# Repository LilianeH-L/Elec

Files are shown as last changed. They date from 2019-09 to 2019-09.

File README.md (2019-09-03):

# Metis-Elec

Repositories pour de le code de l'équipe électrique les trois équipes sont : 

- Acquisiton 
    - Capter les signaux EMG du patient pour le transmettre au Jetson

- Moor_Control
    - Contrôle de la position de tous les moteurs pour ateindre la position désiré

- BLDC_Driver
    - Contrôle individuelle de chaque moteur BLDC pour qu'il soit à la position recquise.

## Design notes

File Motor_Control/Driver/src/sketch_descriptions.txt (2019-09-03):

elctrodesRead : Lecture d'une electrode sur le bicep pour controller un le moteur
elctrodesRead_2 : Lecture d'une electrode sur le bicep pour controller un le moteur

motorController_main : 
motorController_master : Send a command to the motor
motorController_slave : 
motorTest : To test a motor

oldSketches : Older sketches, not useful anymore

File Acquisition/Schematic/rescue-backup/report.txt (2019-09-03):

Info: Backing up file “C:\Users\Victor\Documents\Ecole\Projets\Metis\Metis-Exoskeleton\Acquisition\Schematic\sym-lib-table” to file “C:\Users\Victor\Documents\Ecole\Projets\Metis\Metis-Exoskeleton\Acquisition\Schematic\rescue-backup\sym-lib-table-2018-11-21-18-34-24”.
Info: Backing up file “C:\Users\Victor\Documents\Ecole\Projets\Metis\Metis-Exoskeleton\Acquisition\Schematic\AmpFil3a.sch” to file “C:\Users\Victor\Documents\Ecole\Projets\Metis\Metis-Exoskeleton\Acquisition\Schematic\rescue-backup\AmpFil3a-2018-11-21-18-34-24.sch”.
Info: Backing up file “C:\Users\Victor\Documents\Ecole\Projets\Metis\Metis-Exoskeleton\Acquisition\Schematic\AmpFil3a.pro” to file “C:\Users\Victor\Documents\Ecole\Projets\Metis\Metis-Exoskeleton\Acquisition\Schematic\rescue-backup\AmpFil3a-2018-11-21-18-34-24.pro”.
Info: Backing up file “C:\Users\Victor\Documents\Ecole\Projets\Metis\Metis-Exoskeleton\Acquisition\Schematic\AmpFil3a-cache.lib” to file “C:\Users\Victor\Documents\Ecole\Projets\Metis\Metis-Exoskeleton\Acquisition\Schematic\rescue-backup\AmpFil3a-cache-2018-11-21-18-34-24.lib”.
Info: Backing up file “C:\Users\Victor\Documents\Ecole\Projets\Metis\Metis-Exoskeleton\Acquisition\Schematic\AmpFil3a-rescue.lib” to file “C:\Users\Victor\Documents\Ecole\Projets\Metis\Metis-Exoskeleton\Acquisition\Schematic\rescue-backup\AmpFil3a-rescue-2018-11-21-18-34-24.lib”.
Info: Backing up file “C:\Users\Victor\Documents\Ecole\Projets\Metis\Metis-Exoskeleton\Acquisition\Schematic\AmpFil3a-rescue.dcm” to file “C:\Users\Victor\Documents\Ecole\Projets\Metis\Metis-Exoskeleton\Acquisition\Schematic\rescue-backup\AmpFil3a-rescue-2018-11-21-18-34-24.dcm”.
Info: Adding library “AmpFil3a-rescue”, file “${KIPRJMOD}/AmpFil3a-rescue.lib” to project symbol library table.
Symbol “LM324” mapped to symbol library “AmpFil3a-rescue”.
Symbol “R” mapped to symbol library “AmpFil3a-rescue”.
Symbol “R” mapped to symbol library “AmpFil3a-rescue”.
Symbol “R” mapped to symbol library “AmpFil3a-rescue”.
Symbol “R” mapped to symbol library “AmpFil3a-rescue”.
Symbol “GNDREF” mapped to symbol library “AmpFil3a-rescue”.
Symbol “GNDREF” mapped to symbol library “AmpFil3a-rescue”.
Symbol “C” mapped to symbol library “AmpFil3a-rescue”.
Symbol “INA128” mapped to symbol library “AmpFil3a-rescue”.
Symbol “R” mapped to symbol library “AmpFil3a-rescue”.
Symbol “LM324” mapped to symbol library “AmpFil3a-rescue”.
Symbol “C” mapped to symbol library “AmpFil3a-rescue”.
Symbol “R” mapped to symbol library “AmpFil3a-rescue”.
Symbol “R” mapped to symbol library “AmpFil3a-rescue”.
Symbol “GNDREF” mapped to symbol library “AmpFil3a-rescue”.
Symbol “R” mapped to symbol library “AmpFil3a-rescue”.
Symbol “LM324” mapped to symbol library “AmpFil3a-rescue”.
Symbol “C” mapped to symbol library “AmpFil3a-rescue”.
Symbol “GNDREF” mapped to symbol library “AmpFil3a-rescue”.
Symbol “R” mapped to symbol library “AmpFil3a-rescue”.
Symbol “GNDREF” mapped to symbol library “AmpFil3a-rescue”.
Symbol “Audio-Jack-3” mapped to symbol library “AmpFil3a-rescue”.
Symbol “Conn_01x03” mapped to symbol library “AmpFil3a-rescue”.
Symbol “R” mapped to symbol library “AmpFil3a-rescue”.
Symbol “R” mapped to symbol library “AmpFil3a-rescue”.
Symbol “R” mapped to symbol library “AmpFil3a-rescue”.
Info: Symbol library table mapping complete!

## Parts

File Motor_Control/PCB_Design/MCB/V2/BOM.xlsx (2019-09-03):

Commande Digikey
Qté | Coût | Qté à commander | Coût total | Référence | Description | # Digikey
6 | $2.31 | 6 | $13.86 | Q1-Q6 | N MOSFET | IRLB8743PBF
5 | $0.01 | 5 | $0.05 | R1-R5 | 1K Resistor, 1206 | RNCP1206FTD1K00TR-ND
1 | $1.73 | 1 | $1.73 | R6 | 0.025R Resistor, 5W, 2512 | 2019-TLRH3APTTE25L0FCT-ND
2 | $0.10 | 2 | $0.20 | C1,C3,C6 | 0.1uF Cap |  | Nombre de board à monter | 1
1 | $0.10 | 1 | $0.10 | C2 | 470 uF Electrolytique |  | Coût total | $60.62
2 | $0.10 | 2 | $0.20 | C4,C5 | 1uF Cap
1 | $4.35 | 1 | $4.35 | U1 | DRV8308 | DRV8308RHAR
2 | $1.68 | 2 | $3.36 |  | DIP, Female | XG4M-1030-T
1 | $1.94 | 1 | $1.94 | - | DIP, Male | XG4A-1034
1 | $0.85 | 1 | $0.85 |  | Molex, Female | 353180820
2 | $0.61 | 2 | $1.22 | - | Molex, Male | 39012080
8 | $0.26 | 8 | $2.08 | - | Molex, 22-28 crimp | 39-00-0047
14 | $0.27 | 14 | $3.78 | - | Molex, 18-24 crimp | 39-00-0039
1 | $1.27 | 1 | $1.27 | - | Ribbon Cable, 10, 1' | 3365/10 300
10 | $0.92 | 10 | $9.20 | - | 18 awg wire, 10' | 81044/12-18-9
1 | $2.04 | 1 | $2.04 | - | Male Headers, 40 | 61304011121
1 | $4.80 | 1 | $4.80 |  | SN75175 | SN75175N
1 | $0.89 | 1 | $0.89 |  | SN74LVC245A | SN74LVC245AN
1 | $2.31 | 1 | $2.31 |  | Female Header, 32 | 61303211821
2 | $2.47 | 2 | $4.94 |  | Molex 3, Female | 39303037
2 | $0.72 | 2 | $1.44 |  | Molex 3, Male | 39014031
 | *Rsense : 696-1675-1-ND. 3W

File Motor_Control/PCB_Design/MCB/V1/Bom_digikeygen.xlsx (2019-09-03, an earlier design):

Manufacturer Part Number | Manufacturer | Digi-Key Part Number | Customer Reference | Reference Designator | Packaging | Part Status | Quantity | Unit Price | Extended Price | Quantity Available | Description
IRLB8743PBF | Infineon Technologies | IRLB8743PBF-ND |  | Q1-Q6 | Tube | Active | 6 | 2.31 | $13.86 | 10058 | MOSFET N-CH 30V 78A TO220AB
CF14JT1K00 | Stackpole Electronics Inc | CF14JT1K00CT-ND |  | R1-R5 | Cut Tape (CT) | Active | 5 | 0.15 | $0.75 | 928873 | RES 1K OHM 1/4W 5% AXIAL
630HR025E | Ohmite | 630HR025E-ND |  | R6 | Bulk | Active | 1 | 1.4 | $1.40 | 5138 | RES 0.025 OHM 3W 3% AXIAL
RDER71E104K0K1H03B | Murata Electronics North America | 490-8808-ND |  | C1,C3,C6 | Bulk | Active | 2 | 0.6 | $1.20 | 3313 | CAP CER 0.1UF 25V X7R RADIAL
UKL1E471KHD | Nichicon | 493-13401-ND |  | C2 | Bulk | Active | 1 | 1.26 | $1.26 | 756 | CAP ALUM 470UF 10% 25V RADIAL
FG18X7R1E105KRT06 | TDK Corporation | 445-173261-1-ND |  | C4,C5 | Cut Tape (CT) | Active | 2 | 0.45 | $0.90 | 7135 | CAP CER 1UF 25V X7R RADIAL
DRV8308RHAR | Texas Instruments | 296-37834-1-ND |  | U1 | Cut Tape (CT) | Active | 1 | 4.35 | $4.35 | 257 | IC MOTOR DRIVER 8.5V-32V 40VQFN
XG4M-1030-T | Omron Electronics Inc-EMC Div | OR909-ND |  |  | Tray | Active | 2 | 1.68 | $3.36 | 27951 | CONN RCPT 10POS IDC 28AWG GOLD
XG4A-1034 | Omron Electronics Inc-EMC Div | OR1001-ND |  | - | Tray | Active | 1 | 1.94 | $1.94 | 8374 | CONN HEADER R/A 10POS 2.54MM
0353180820 | Molex | WM13197-ND |  |  | Bag | Active | 1 | 0.85 | $0.85 | 6463 | CONN HEADER R/A 8POS 4.2MM
0039012080 | Molex | WM3703-ND |  | - | Bulk | Active | 2 | 0.61 | $1.22 | 66365 | CONN RECEPT 8POS DUAL
39-00-0047 | Molex | WM2503-ND |  | - | Bulk | Active | 8 | 0.26 | $2.08 | 111858 | CONN SOCKET 22-28AWG CRIMP TIN
39-00-0039 | Molex | WM2501-ND |  | - | Bulk | Active | 14 | 0.257 | $3.59 | 515333 | CONN SOCKET 18-24AWG CRIMP TIN
81044/12-18-9 | TE Connectivity Aerospace, Defense and Marine | A132409-DS-ND |  | - | * | Active | 10 | 0.728 | $7.28 | 4742 | HOOK-UP STRND 18AWG WHITE FT
61304011121 | Wurth Electronics Inc. | 732-5334-ND |  | - | Bag | Active | 1 | 2.04 | $2.04 | 1805 | CONN HEADER VERT 40POS 2.54MM
SN75175N | Texas Instruments | 296-1736-5-ND |  |  | Tube | Active | 1 | 4.8 | $4.80 | 2808 | IC QUAD DIFF LINE RECEIVER 16DIP
SN74LVC245AN | Texas Instruments | 296-8503-5-ND |  |  | Tube | Active | 1 | 0.89 | $0.89 | 3388 | IC TXRX NON-INVERT 3.6V 20DIP
61303211821 | Wurth Electronics Inc. | 732-2860-ND |  |  | Tray | Active | 1 | 2.31 | $2.31 | 257 | CONN HDR 32POS 0.1 GOLD PCB
0039303037 | Molex | WM23935-ND |  |  | Bag | Active | 2 | 2.47 | $4.94 | 1379 | CONN HEADER R/A 3POS 4.2MM
0039014031 | Molex | WM23608-ND |  |  | Bag | Active | 2 | 0.72 | $1.44 | 16106 | CONN RECEPT 3POS VERT SINGLE
3365/10 300 | 3M | 3M157815-5-ND |  |  | Bulk | Active | 1 | 4.54 | $4.54 | 0 | CBL RIBN 10COND 0.050 GRAY 5'
D2816-42 | Harwin Inc. | 952-2211-ND |  |  | Tube | Active | 1 | 1.93 | $1.93 | 630 | CONN IC DIP SOCKET 16POS GOLD
D2820-42 | Harwin Inc. | 952-2213-ND |  |  | Tube | Active | 1 | 2.26 | $2.26 | 84 | CONN IC DIP SOCKET 20POS GOLD

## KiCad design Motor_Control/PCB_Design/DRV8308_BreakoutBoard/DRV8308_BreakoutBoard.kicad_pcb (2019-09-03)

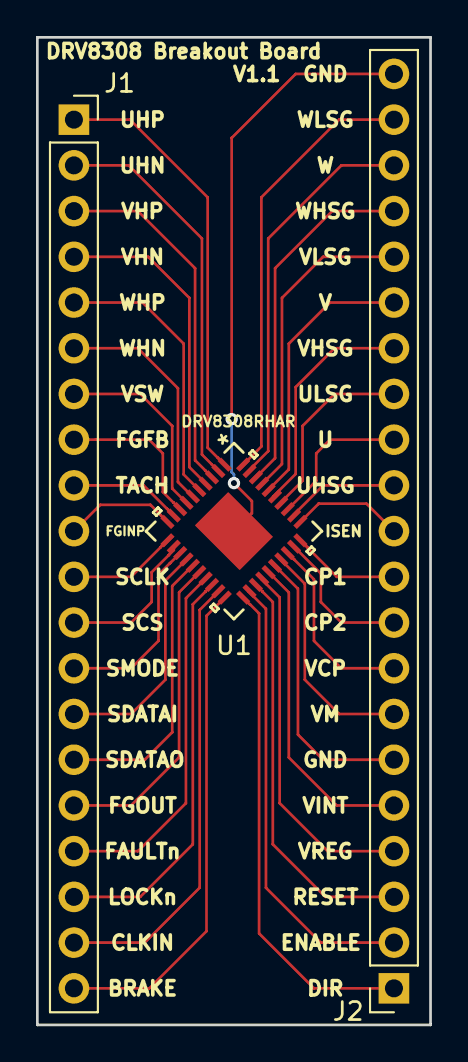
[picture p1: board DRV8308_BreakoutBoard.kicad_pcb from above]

Board: 2 copper layers, 21.8 x 54.9 mm, 3 parts (0 on the bottom side), 41 nets.

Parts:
J1: Conn_01x20_Female; PinSocket_1x20_P2.54mm_Vertical
J2: Conn_01x21_Female; PinSocket_1x21_P2.54mm_Vertical
U1: DRV8308RHAR

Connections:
unnamed: J1.1, U1.1
unnamed: J1.2, U1.2
unnamed: J1.3, U1.3
unnamed: J1.4, U1.4
unnamed: J1.5, U1.5
unnamed: J1.6, U1.6
unnamed: J1.7, U1.7
unnamed: J1.8, U1.8
unnamed: J1.9, U1.9
unnamed: J1.10, U1.10
unnamed: J1.11, U1.11
unnamed: J1.12, U1.12
unnamed: J1.13, U1.13
unnamed: J1.14, U1.14
unnamed: J1.15, U1.15
unnamed: J1.16, U1.16
unnamed: J1.17, U1.17
unnamed: J1.18, U1.18
unnamed: J1.19, U1.19
unnamed: J1.20, U1.20
unnamed: J2.1, U1.21
unnamed: J2.2, U1.22
unnamed: J2.3, U1.23
unnamed: J2.4, U1.24
unnamed: J2.5, U1.25
unnamed: J2.6, U1.26
unnamed: J2.7, U1.27
unnamed: J2.8, U1.28
unnamed: J2.9, U1.29
unnamed: J2.10, U1.30
unnamed: J2.11, U1.31
unnamed: J2.12, U1.32
unnamed: J2.13, U1.33
unnamed: J2.14, U1.34
unnamed: J2.15, U1.35
unnamed: J2.16, U1.36
unnamed: J2.17, U1.37
unnamed: J2.18, U1.38
unnamed: J2.19, U1.39
unnamed: J2.20, U1.40
unnamed: J2.21, U1.41

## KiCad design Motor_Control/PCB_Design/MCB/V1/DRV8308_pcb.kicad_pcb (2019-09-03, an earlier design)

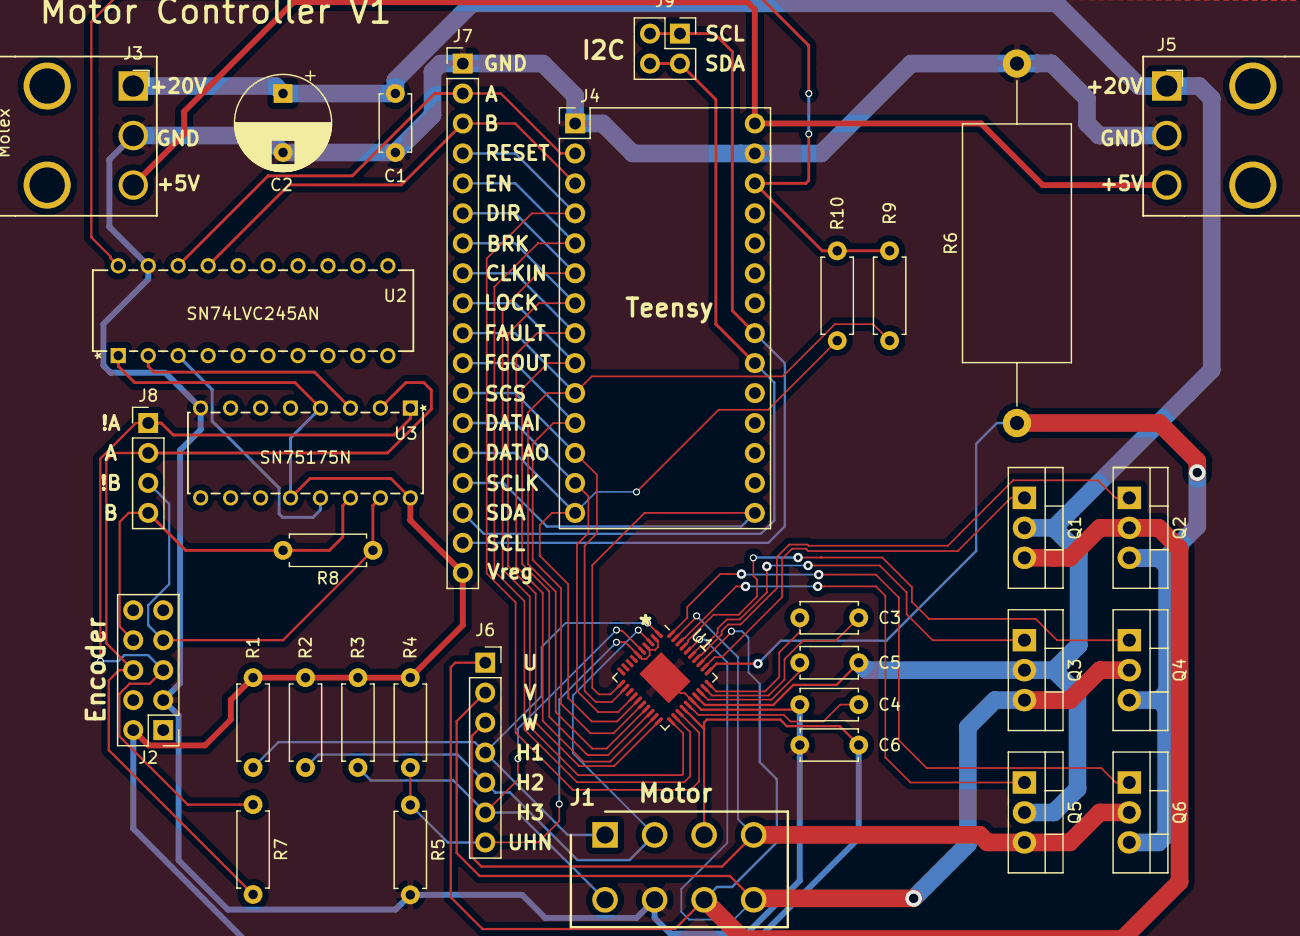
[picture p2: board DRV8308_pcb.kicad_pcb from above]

Board: 2 copper layers, 34 parts (0 on the bottom side), 45 nets.

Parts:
C1, C3, C6: 0.1uF; C_Disc_D4.7mm_W2.5mm_P5.00mm
C2: 470uF; CP_Radial_D8.0mm_P5.00mm
C4, C5: 1uF; C_Disc_D4.7mm_W2.5mm_P5.00mm
J1: Molex_Motor; SHDR8W125P550X420_2X4_1800X960X1310P
J2: Conn_Encoder; PinHeader_2x05_P2.54mm_Vertical
J3: Molex_Pwr_In; Molex,1x3
J4: Teensy; TeensyLC
J5: Molex_Pwr_Out; Molex,1x3,Right
J6: Conn_01x07_Female; PinSocket_1x07_P2.54mm_Vertical
J7: PinsTeensy; PinHeader_1x18_P2.54mm_Vertical
J8: PinsEncoder; PinHeader_1x04_P2.54mm_Vertical
J9: Conn_I2C; PinSocket_2x02_P2.54mm_Vertical
Q1, Q2, Q3, Q4, Q5, Q6: Q_NMOS_IRLB8743; TO-220-3_Vertical
R1, R2, R3, R4, R5: 1K; R_Axial_DIN0207_L6.3mm_D2.5mm_P7.62mm_Horizontal
R6: 0.025; R_Axial_DIN0922_L20.0mm_D9.0mm_P30.48mm_Horizontal
R7, R8: 120; R_Axial_DIN0207_L6.3mm_D2.5mm_P7.62mm_Horizontal
R9, R10: 4.7k; R_Axial_DIN0207_L6.3mm_D2.5mm_P7.62mm_Horizontal
U1: DRV8308; Texas_S-PVQFN-N40_EP3.52x2.62mm
U2: SN74LVC245AN
U3: SN75175N

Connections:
/3.3V: J4.26, R9.2, R10.2, U2.20
/A: J4.2, J7.2, U2.18
/B: J4.3, J7.3, U2.17
/BRAKE: J4.7, J7.7, U1.20
/CLKIN: J4.8, J7.8, U1.19
/DATAI: J4.13, J7.13, U1.14
/DATAO: J4.14, J7.14, R10.1, U1.15
/DIR: J4.6, J7.6, U1.21
/ENABLE: J4.5, J7.5, U1.22
/ENC_!A: J2.5, J8.1, R7.1, U3.1
/ENC_!B: J2.7, J8.3, R8.1, U3.15
/ENC_A: J2.6, J8.2, R7.2, U3.2
/ENC_B: J2.8, J8.4, R8.2, U3.14
/FAULTn: J4.10, J7.10, R9.1, U1.17
/FGOUT: J4.11, J7.11, U1.16
/Hall_1: J1.1, J6.4, R1.2, U1.1
/Hall_2: J1.2, J6.5, R2.2, U1.3
/Hall_3: J1.5, J6.6, R3.2, U1.5
/LOCKn: J4.9, J7.9, U1.18
/Power/ISEN: Q2.3, Q4.3, Q6.3, R6.1, U1.31
/Power/UHSG: Q1.1, U1.32
/Power/ULSG: Q2.1, U1.34
/Power/VHSG: Q3.1, U1.35
/Power/VLSG: Q4.1, U1.37
/Power/WHSG: Q5.1, U1.38
/Power/WLSG: Q6.1, U1.40
/RESET: J4.4, J7.4, U1.23
/SCL: J4.21, J7.17, J9.1, J9.2
/SCLK: J4.15, J7.15, U1.11
/SCS: J4.12, J7.12, U1.12
/SDA: J4.20, J7.16, J9.3, J9.4
/UHN: J6.7, R4.2, R5.1, U1.2, U1.4, U1.6
/Vin: J3.3, J4.28, J5.3
/Vm: C1.1, C2.1, C5.1, J3.1, J5.1, Q1.2, Q3.2, Q5.2, U1.27
/Vreg: C6.2, J1.3, J2.2, J7.18, R1.1, R2.1, R3.1, R4.1, U1.24, U2.1, U3.4, U3.12, U3.16
GNDREF: C1.2, C2.2, C4.1, C6.1, J1.6, J2.3, J3.2, J4.1, J4.27, J5.2, J7.1, R5.2, R6.2, U1.26, U1.41, U2.19, U3.8
Motor_1: J1.7, J6.1, Q1.3, Q2.2, U1.33
Motor_2: J1.8, J6.2, Q3.3, Q4.2, U1.36
Motor_3: J1.4, J6.3, Q5.3, Q6.2, U1.39
unnamed: C3.1, U1.30
unnamed: C3.2, U1.29
unnamed: C4.2, U1.25
unnamed: C5.2, U1.28
unnamed: U2.2, U3.3
unnamed: U2.3, U3.13

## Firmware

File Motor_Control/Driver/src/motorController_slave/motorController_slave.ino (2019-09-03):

/*
Cr�� le 18/03/2019
Auteurs : Charles et Maude

Code pour controller un moteur en mode slave par I2C

Commandes pouvant �tre entr�es "#___": 
	Moteur
resetAngle : Set encoder to 0
readRegisters : Print the values of the registers
stop : Activate brake pin

	PID
togglePrint : Affiche les valeurs du PID ou non
setkp : Pour changer la valeur de kp
setki : Pour changer la valeur de ki
setkd : Pour changer la valeur de kd

Autres :
Entrer '=x' : Set encoder value to x
Entrer 'x' : Set goal to x

*/
#define ENCODER_OPTIMIZE_INTERRUPTS

#include <WireKinetis.h>
#include <Wire.h>
#include <SPI.h>
#include <PID_v1.h>
#include <Encoder.h>

/*
#pragma region "Prototypes" //{
//Fonctions SPI
void writeRegister(byte reg, byte value1, byte value2);
unsigned int readRegister(byte reg);
void SPISetup();
void motorSetup();
void readRegisters();


//Fonctions qui fonctionnent :
double readAngle(bool fullTurn);
void updateAngle(double newAngle, double& angle);
void resetAngle();
void checkIfFullTurn(double& angle);

void readSerial(double& angle);
void executeCommande(String commande);

#pragma endregion //}*/

#pragma region "Variables et constantes" //{

//SPI communication
const byte READ = 0b10000000;
const byte WRITE = 0b00000000;
const byte faultReg = 0x2a;
const int maxSpeed = 480000; //Speed of the SPI (HZ)
const int CS = 10;
const byte registersAdress[] = {0x00,0x02,0x03,0x04,0x05,0x06,0x07,0x08,0x09,0x0A,0x0B,0x2A };
//const byte defaultValues[] = {0x0111,0x04FF,0x6800,0x00D7,0x0000,0x0000,0x0000,0x0000,0x0000,0xF000,0x0000,0x0000 };


//Moteur
const int resetPin = 2;
const int enablePin = 3;
const int directionPin = 4;
const int brakePin = 5;
const int motorPin = 6;
const int lockPin = 7;
const int faultPin = 8;
const int encoderPin1 = 1, encoderPin2 = 0;

//Lecture de l'encoder
const double gearReduction = 1; //100 with gearbox, 1 without
const double encoderResolution = 4;
const double countsPerTurn = 800;

//Contr�le du moteur
const int pulseMax = 2047;
const int pulseMin = 100;
const int turnCW = 1;
const int turnCCW = 2;


//Conraintes sur les angles max et min
const int angleMax = 400;
const int angleMin = -10;

//PID
double setpoint, input, output;
double kp = 0.5;
double ki = 0;
double kd = 0;
double goal = 10000; //Variation in angle to go
bool autoPilot = false;
bool goingUp = true;	//Direction of autopilot
bool toPrint = true;

PID myPID(&input, &output, &setpoint, kp, ki, kd, DIRECT);		//PID(&Input, &Output, &Setpoint, Kp, Ki, Kd, Direction) Option to allow Proportional on measurment
IntervalTimer timer;
Encoder encoder(encoderPin2, encoderPin1);
double speed = 0;
double position = 0;

#pragma endregion //}


void toggleGoal()
{
	goal *= -1;
}

void setup() {
	Serial.begin(9600);
	Serial.println("Starting");

  pinMode(3, OUTPUT);
  digitalWrite(3, HIGH);
  
	SPISetup();
  //I2CSetup();
	//motorSetup();
	//PIDSetup();


	timer.begin(toggleGoal, 500000);

  
}

/*
void binaryControl()
{
	readSerial(goal);
	setpoint = goal;
	position = encoder.read();
	int delta = position - setpoint;
	setDirection(delta < 0);
	if (abs(delta) > 100)
	{
		// digitalWrite(brakePin, LOW);
		analogWrite(motorPin, 400);
	}
	else 
	{
		analogWrite(motorPin, 0);
		// digitalWrite(brakePin, HIGH);
		Serial.println(position);
	}
		

}*/

void loop() {
	//binaryControl();
  //readFault();
  //delay(1000);
  //readRegisters();
  Serial.println(encoder.read());
	//pidControl();
	//  setDirection(turnCW);
	//  analogWrite(motorPin, 500);
	//  Serial.println(readAngle(speed));
}

#pragma region "Setup and SPI" //{
void writeRegister(byte reg, byte value1, byte value2) {

	byte toSend = WRITE | reg;

	SPI.beginTransaction(SPISettings(maxSpeed, MSBFIRST, SPI_MODE0));
	digitalWrite(CS, HIGH);
	delayMicroseconds(1);

	//send write command + reg adress
	SPI.transfer(toSend);

	//send first 8 bits (MSB)
	SPI.transfer(value1);
	//send last 8 bits (LSB)
	SPI.transfer(value2);

	digitalWrite(CS, LOW);
	SPI.endTransaction();
}

unsigned int readRegister(byte reg) {
	byte toRead = READ | reg;

	SPI.beginTransaction(SPISettings(maxSpeed, MSBFIRST, SPI_MODE0));
	digitalWrite(CS, HIGH);
	delayMicroseconds(1);
	//send read command + reg adress
	SPI.transfer(toRead);

	int result;
	byte readValue;

	//get first 8 bits of data (MSB)
	readValue = SPI.transfer(0x00);
	result = readValue << 8;
	//get last 8 bits of data (LSB)
	readValue = SPI.transfer(0x00);

	//combine into 16 bits result
	result = result | readValue;

	digitalWrite(CS, LOW);
	SPI.endTransaction();

	return (result);
}

void readRegisters() {
	//To Read the registers
	Serial.println("Lecture des registres");
	Serial.println(readRegister(0x00), HEX);
	Serial.println(readRegister(0x02), HEX);
	Serial.println(readRegister(0x03), HEX);
	Serial.println(readRegister(0x04), HEX);
	Serial.println(readRegister(0x0A), HEX);
	Serial.println();
	Serial.println();
}

void SPISetup() {
	//SPI Setup
	pinMode(CS, OUTPUT);
	SPI.begin();
	writeRegisters();
	//Recommended setup
  
}

void writeRegisters() {
	writeRegister(0x00, 0x01, 0x11);
	//writeRegister(0x01,0x00,0x00);
	writeRegister(0x02, 0x04, 0xFF);
	writeRegister(0x03, 0x68, 0x00);
	writeRegister(0x04, 0x00, 0xD7);
	writeRegister(0x05, 0x00, 0x00);
	writeRegister(0x06, 0x00, 0x00);
	writeRegister(0x07, 0x00, 0x00);
	writeRegister(0x08, 0x00, 0x00);
	writeRegister(0x09, 0x00, 0x00);
	writeRegister(0x0A, 0xF0, 0x00);
	writeRegister(0x0B, 0x00, 0x00);
	writeRegister(0x2A, 0x00, 0x00);
}

void readFault() {
	if (digitalRead(faultPin) == HIGH) {
		Serial.println("Il y a une faute :(");
	}
	else
		Serial.print("Pas de faute");

	Serial.print("Le registre de faute est : ");
	Serial.println(readRegister(0x2A), BIN);
}

void writeDefaultRegisters() {
	//Recommended setup
	writeRegister(0x00, 0x01, 0x11);
	//writeRegister(0x01,0x00,0x00);
	writeRegister(0x02, 0x04, 0xFF);
	writeRegister(0x03, 0x68, 0x00);
	writeRegister(0x04, 0x00, 0xD7);
	writeRegister(0x05, 0x00, 0x00);
	writeRegister(0x06, 0x00, 0x00);
	writeRegister(0x07, 0x00, 0x00);
	writeRegister(0x08, 0x00, 0x00);
	writeRegister(0x09, 0x00, 0x00);
	writeRegister(0x0A, 0xF0, 0x00);
	writeRegister(0x0B, 0x00, 0x00);
	writeRegister(0x2A, 0x00, 0x00);
}

/*
void checkRegisters() {
	bool registersOk = true;
	for (int i = 0; i < 12; i++) {
		if (readRegister(registersAdress[i] != defaultValues[i]))
			registersOk = false;
	}
	if (registersOk)
		Serial.println("Les registres ont �t� bien �crit");
	else
		Serial.println("Erreur lors de l'�criture des registres");
}
*/

/*
void motorSetup() {
	//Motor Setup
	pinMode(2, OUTPUT);
	pinMode(3, OUTPUT);
	pinMode(4, OUTPUT);
	pinMode(5, OUTPUT); //Brake
	pinMode(6, OUTPUT); //Motor
	pinMode(7, INPUT);
	pinMode(8, INPUT);

	analogWriteResolution(11);
	analogWriteFrequency(motorPin, 23437.5); //Values between 0-2047

	digitalWrite(2, LOW); //RESET
	digitalWrite(3, HIGH); //Enable
	digitalWrite(4, HIGH); //DIR
	digitalWrite(5, LOW); //Brake
}

void PIDSetup() {
	input = 0;
	setpoint = 0;
	myPID.SetMode(AUTOMATIC);
	myPID.SetOutputLimits(-2047, 2047);
}

#pragma endregion //}

#pragma region "Encoder" //{

//TESTER : Pour old controller, Fonction qui retourne l'angle du moteur, If fullTurn = true, will convert the angle to a circle (0-360), false for no correction

double countToAngleFactor = 360.0 / (countsPerTurn*gearReduction*encoderResolution);
double readAngle(bool fullTurn) {
	double count;
	//double angle;
	count = encoder.read();    //To count
	double angle =  encoder.read()*countToAngleFactor ; //To get degrees

	//if (fullTurn)
	//	checkIfFullTurn(angle);

	return angle;
}

//Fonction pour reset la position � chaque tour
//TODO: s'assurer qu'il n'y aille plus d'angle n�gatif en v�rifiant avant de corriger
void checkIfFullTurn(double& angle) {

	if (angle > 360) {
		encoder.write(0);
	}

	else if (angle < -0.0001) {
		encoder.write(3200 * gearReduction);
	}
}

//Fonction pour updater l'angle s'il change et l'afficher
void updateAngle(double newAngle, double& angle) {
	if (newAngle != angle) {
		Serial.print("Angle = ");
		Serial.println(newAngle);
		angle = newAngle;
	}
}

#pragma endregion //}

#pragma region "Motor" //{

void setDirection(bool direction){
	if (direction)
		digitalWrite(directionPin, HIGH);
	else
		digitalWrite(directionPin, LOW);
}

#pragma endregion //}

#pragma region "PID" //{


void pidControl() {
	//readSerial(goal);
	setpoint = goal;
	position = encoder.read();

	//Update input with the Angle
	input = goal - position;

	//Compute 
	myPID.Compute();

	//Check the direction to turn
	if (output > 0) {
		setDirection(turnCCW);
		speed = output;
	}
	else if (output < 0) {
		setDirection(turnCW);
		speed = -output;
	}
	 Serial.print(position);
	 Serial.print("\tsp: ");
	 Serial.println(setpoint);
	//if (toPrint)	
	//	printVariables();

	analogWrite(motorPin, speed);
}

//Fonction pour changer les variables
void setTunings(int kp, int ki, int kd) {
	myPID.SetTunings(kp, ki, kd);
	Serial.print("Kp= ");
	Serial.print(kp);
	Serial.print("	Ki= ");
	Serial.print(ki);
	Serial.print("	Kd= ");
	Serial.println(kd);
}

//To print the variables : setpoint, input, output, speed
void printVariables() {
	Serial.print("Setpoint : ");
	Serial.print(setpoint);
	Serial.print(" Position : ");
	Serial.print(position);
	Serial.print("	Input : ");
	Serial.print(input);
	Serial.print("	Output : ");
	Serial.print(output);
	Serial.print("	Speed : ");
	Serial.print(speed);
	Serial.print(" Direction :");
	Serial.println(digitalRead(directionPin));
}

#pragma endregion//}

#pragma region "Serial Communication" //{
//Read data from the serial port. Return the value if its a number. start with # to call a function, =x to set angle to x, x to set goal new goal
void readSerial(double& angleToGo) {

	String commande;

	while (Serial.available()) {
		char c = Serial.read();  //gets one byte from serial buffer
		commande += c; //makes the string readString
		delay(2);  //slow looping to allow buffer to fill with next character
	}

	if (commande.length() > 0) {
		Serial.println(commande);  //so you can see the captured string 

		if (commande[0] == '#') {
			commande = commande.substring(1);
			Serial.print("Commande : ");
			Serial.println(commande);
			executeCommande(commande);
		}

		if (commande[0] == '=') {
			double angle = double(commande.substring(1).toInt());
			double count = 0;
			count = angle / 360 * countsPerTurn*gearReduction*encoderResolution;
			encoder.write(count);
		}

		else {
			int n = commande.toInt();  //convert readString into a number
			angleToGo = n;
			Serial.print("Angle To go : ");
			Serial.println(angleToGo);
		}
		commande = ""; //empty for next input
	}
}
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

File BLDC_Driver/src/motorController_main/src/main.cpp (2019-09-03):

/*
Cree le 18/03/2019
Auteurs : Charles et Maude

Code pour controller un moteur en mode slave par I2C

Commandes pouvant etre entrees "#___": 
	Moteur
resetAngle : Set encoder to 0
readRegisters : Print the values of the registers
stop : Activate brake pin

	PID
togglePrint : Affiche les valeurs du PID ou non
setkp : Pour changer la valeur de kp
setki : Pour changer la valeur de ki
setkd : Pour changer la valeur de kd

Autres :
Entrer '=x' : Set encoder value to x
Entrer 'x' : Set goal to x

*/
#define ENCODER_OPTIMIZE_INTERRUPTS

#include <Arduino.h>
#include <Wire.h>
#include <SPI.h>
#include <Encoder.h>


#pragma region "Prototypes" //{
//Fonctions SPI
void writeRegister(byte reg, byte value1, byte value2);
void writeRegisters();
unsigned int readRegister(byte reg);
void SPISetup();
void motorSetup();
void readRegisters();
void writeDefaultRegisters();


//Fonctions qui fonctionnent :
inline double readAngle(bool fullTurn);
void updateAngle(double newAngle, double& angle);
void resetAngle();
void checkIfFullTurn(double& angle);

void readSerial(double& angle);

inline void binaryControl(double);
inline void setDirection(bool);
inline void toggleGoal();

#pragma endregion //}

#pragma region "Variables et constantes" //{

//SPI communication
const byte READ = 0b10000000;
const byte WRITE = 0b00000000;
const byte faultReg = 0x2a;
const int maxSpeed = 480000; //Speed of the SPI (HZ)
const int CS = 10;
const byte registersAdress[] = {0x00,0x02,0x03,0x04,0x05,0x06,0x07,0x08,0x09,0x0A,0x0B,0x2A };

//Moteur
const int resetPin = 2;
const int enablePin = 3;
const int directionPin = 4;
const int brakePin = 5;
const int motorPin = 6;
const int lockPin = 7;
const int faultPin = 8;
const int encoderPin1 = 0, encoderPin2 = 1;

//Lecture de l'encoder
const double gearReduction = 1; //100 with gearbox, 1 without
const double encoderResolution = 4;
const double countsPerTurn = 800;

//Controle du moteur
const int pulseMax = 2047;
const int pulseMin = 100;
const int turnCW = 1;
const int turnCCW = 2;

//Conraintes sur les angles max et min
const int angleMax = 400;
const int angleMin = -10;

//Control
IntervalTimer timer;
Encoder encoder(encoderPin2, encoderPin1);
double goal = 10000; //Variation in angle to go
double position = 0;
double setpoint = 0;

unsigned long prevTime = 0;
bool toTurn = false;

bool state = false;

#pragma endregion //}

inline void toggleStateWire(int){
	int data = Wire.read();
	if (data)
		state = true;
	else
		state = false;
}

int comPin = 18;
long upGoal = 500;
long downGoal = 1;



void setup() {
	//Serial.begin(9600);
	//Serial.println("Starting");
  
	SPISetup();
	motorSetup();

	//timer.begin(toggleGoal, 5000000);
	//Wire.begin(155);
	//Wire.onReceive(toggleStateWire);
	pinMode(comPin, INPUT);
	//attachInterrupt(comPin, toggleState, CHANGE);
}

inline void toggleState(){
	Serial.println("Toggling state");
	state = digitalRead(comPin);
}

bool prevState = state;
int count = 0;
int turnTime = 350;
int speed = 400;

inline void timeControl(){
	if(state!=prevState){
		prevState=state;
		count = 0;
		while(count <= turnTime){
			Serial.println(count);
			digitalWrite(enablePin,HIGH);
			digitalWrite(brakePin, LOW);
			analogWrite(motorPin, speed);
			
			if(state){
				setDirection(HIGH);
			}
			else{
				setDirection(LOW);
			}
			count++;
			delay(10);
		}
		digitalWrite(enablePin, LOW);
		digitalWrite(brakePin, HIGH);
	}
}

void loop() {
	//readRegisters();
	// setDirection(true);
	// analogWrite(motorPin, 2048);
	state = digitalRead(comPin);
	//Serial.println(readAngle(false));
	// Serial.print('\t');
	// Serial.println(state);
	timeControl();
	
	// if (state)
	// {
	// binaryControl(upGoal);
	// }
	// else
	// {
	// binaryControl(downGoal);
	// }


}

#pragma region "Setup and SPI" //{

void writeRegister(byte reg, byte value1, byte value2) {

	byte toSend = WRITE | reg;

	SPI.beginTransaction(SPISettings(maxSpeed, MSBFIRST, SPI_MODE0));
	digitalWrite(CS, HIGH);
	delayMicroseconds(1);

	//send write command + reg adress
	SPI.transfer(toSend);

	//send first 8 bits (MSB)
	SPI.transfer(value1);
	//send last 8 bits (LSB)
	SPI.transfer(value2);

	digitalWrite(CS, LOW);
	SPI.endTransaction();
}
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

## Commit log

2019-09-03 Files setup
    [AmpFil3a-2018-11-21-18-34-24.sch, AmpFil3a.sch, BOM.xlsx, Bom_digikeygen.xlsx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]
2019-10-03 Rename folder
    [BOM.xlsx, Bom_digikeygen.xlsx, DRV8308_BreakoutBoard-B.Cu.gbl, DRV8308_BreakoutBoard-B.Cu.gbr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]
2019-10-03 Folder management
    [BOM.xlsx, Bom_digikeygen.xlsx, DRV8308_BreakoutBoard-B.Cu.gbl, DRV8308_BreakoutBoard-B.Cu.gbr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]
2019-10-27 Tentative de mettre les codes
2019-10-31 Add files via upload
    Code de lecture d'un encodeur

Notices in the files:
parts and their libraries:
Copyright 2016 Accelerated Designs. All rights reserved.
